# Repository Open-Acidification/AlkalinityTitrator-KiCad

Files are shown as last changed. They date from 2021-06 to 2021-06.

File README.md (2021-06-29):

# AlkalinityTitrator-KiCad
<!-- ALL-CONTRIBUTORS-BADGE:START - Do not remove or modify this section -->

<!-- ALL-CONTRIBUTORS-BADGE:END -->

KiCad files for pcb design for Open Acidification Alkalinity Titrator unit.

## Software Requirements

1. [KiCad](https://kicad.org/) - The PCB layout was created with KiCad which works on multiple platforms.

## Viewing and Editing the Schematic

1. Clone this repo to your local computer.
1. Open KiCad.
1. Use the KiCad menu to open the `full_project.pro` project file.
    * _File -> Open Project_
    * Navigate to your local repo location and select `full_project.pro` project file.
    * Double click the `full_project.sch` file on the left pane to open Eeschema.
1. View the Schematic.

## Viewing and Editing the PCB

1. Clone this repo to your local computer.
1. Open KiCad.
1. Use the KiCad menu to open the `full_project.pro` project file.
    * _File -> Open Project_
    * Navigate to your local repo location and select `full_project.pro` project file.
    * Double click the `full_project.kicad_pcb` file on the left pane to open Pcbnew.
1. View the PCB.

## Release

Each release has the appropriate binary Gerber (`.gbr`) and Drill (`.drl`) to be sent to the PCB board printing company.

We may have extra printed. Please contact us.

## Related Projects

* Micro Controller - [Alkalinity Titrator](https://github.com/Open-Acidification/AlkalinityTitrator) forms the brain of the device.
* PCB - __This repo__ holds the specifications for the PCB which connects various sensors.

## Contributors ✨

Thanks goes to these wonderful people ([emoji key](https://allcontributors.org/docs/en/emoji-key)):

<!-- ALL-CONTRIBUTORS-LIST:START - Do not remove or modify this section -->
<!-- prettier-ignore-start -->
<!-- markdownlint-disable -->
<table>
  <tr>
    <td align="center"><a href="https://github.com/KonradMcClure"><br /><sub><b>Konrad McClure</b></sub></a><br /><a href="https://github.com/Open-Acidification/AlkalinityTitrator-KiCad/commits?author=KonradMcClure" title="Code">💻</a></td>
    <td align="center"><a href="https://github.com/Noah-Griffith"><br /><sub><b>Noah-Griffith</b></sub></a><br /><a href="https://github.com/Open-Acidification/AlkalinityTitrator-KiCad/commits?author=Noah-Griffith" title="Code">💻</a></td>
  </tr>
</table>

<!-- markdownlint-restore -->
<!-- prettier-ignore-end -->

<!-- ALL-CONTRIBUTORS-LIST:END -->

This project follows the [all-contributors](https://github.com/all-contributors/all-contributors) specification. Contributions of any kind welcome!

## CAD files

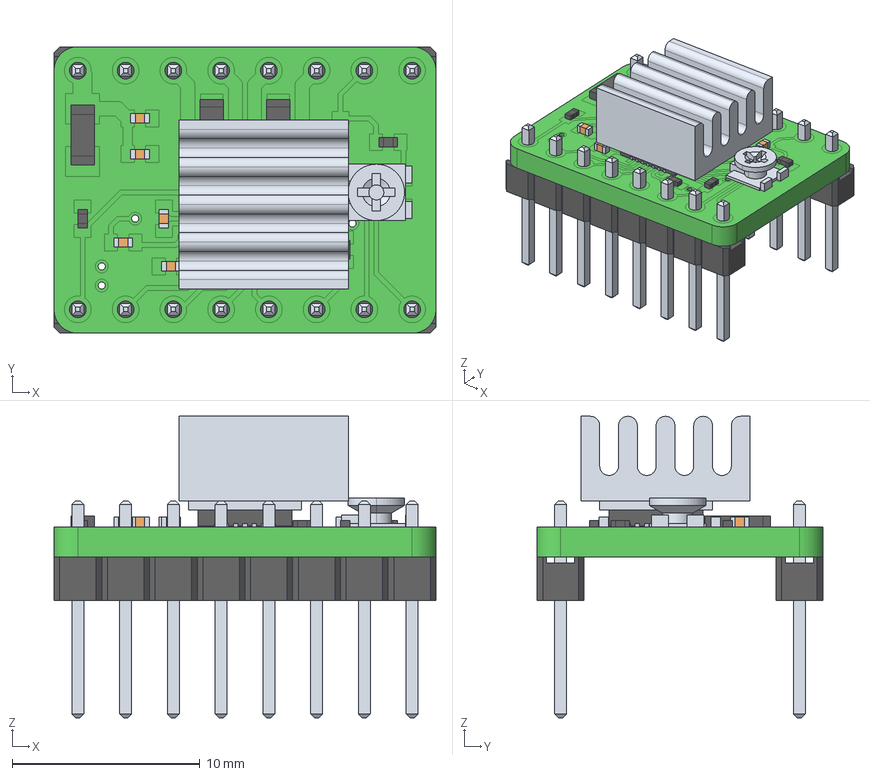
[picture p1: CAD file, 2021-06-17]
imported_3d/stepstick_asm.stp
20.3 x 15.2 x 16.0 mm
SCULPT1_1_-10289 x 6
SCULPT1_3_-13682 x 6
SCULPT1_2_-26742 x 6
0805_RESISTOR x 2
0402RES_RESISTOR0402RES x 4
LPATTERN1_1_ x 2
LPATTERN1_6_ x 2
LPATTERN1_7_ x 2
LPATTERN1_3_ x 2
LPATTERN1_2_ x 2
LPATTERN1_5_ x 2
LPATTERN1_8_ x 2
LPATTERN1_14_ x 2
LPATTERN1_10_ x 2
LPATTERN1_13_ x 2
LPATTERN1_4_ x 2
LPATTERN1_11_ x 2
LPATTERN1_9_ x 2
LPATTERN1_12_ x 2
SCULPT1_4_
SCULPT1_15_
SCULPT1_3_-1394
SCULPT1_1_-1765
SCULPT1_29_
SCULPT1_11_
SCULPT1_21_
SCULPT1_12_
SCULPT1_13_
SCULPT1_23_
SCULPT1_25_
SCULPT1_16_
SCULPT1_14_
SCULPT1_22_
SCULPT1_26_
SCULPT1_10_
SCULPT1_18_
SCULPT1_28_
SCULPT1_7_
SCULPT1_17_
SCULPT1_24_
SCULPT1_20_
SCULPT1_8_
SCULPT1_6_
SCULPT1_19_
SCULPT1_9_
SCULPT1_27_
SCULPT1_5_
SCULPT1_1_-7052
SCULPT1_2_-11434
SCULPT1_3_-28930
STEPSTICK-2620
HEATSINK_FOR_A4988
1206_CAP1206

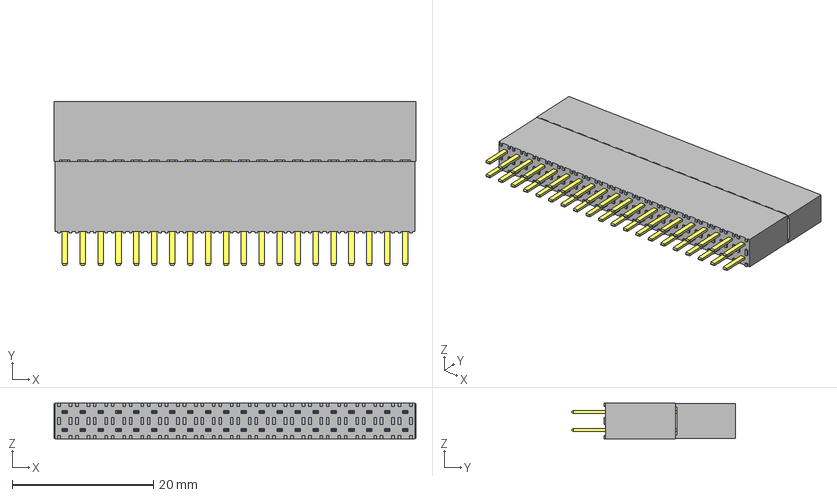
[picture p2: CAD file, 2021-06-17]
imported_3d/ESW-120-44-L-D.stp
51.3 x 23.2 x 5.08 mm
_ESW-120-44-L-D_socket
_ESW-120-44-L-D_pins
_ESW-120-44-L-D_bsocket

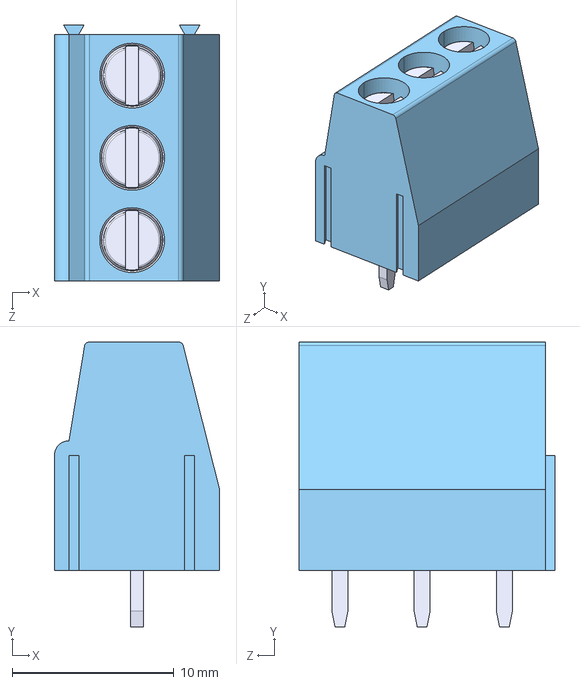
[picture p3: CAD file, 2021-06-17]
imported_3d/CUI_DEVICES_TB004-508-03BE.step
10.2 x 17.6 x 15.8 mm

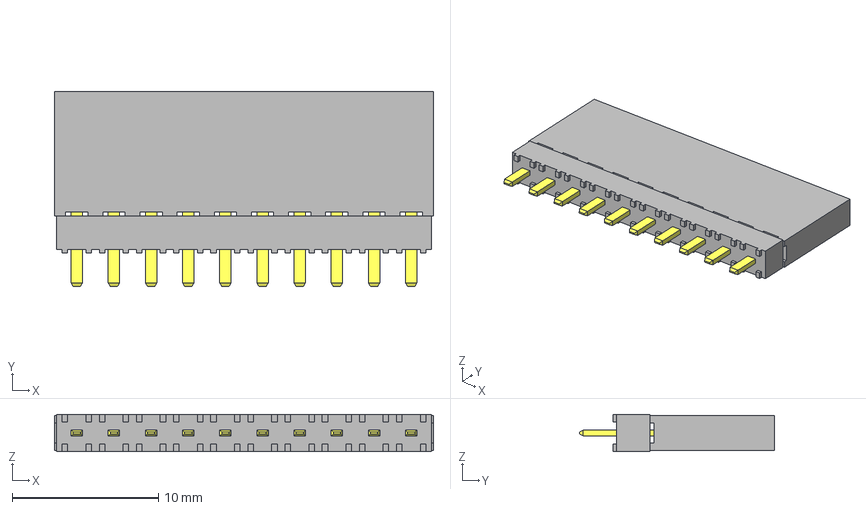
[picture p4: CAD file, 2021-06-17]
imported_3d/ESW-110-12-L-S.stp
25.9 x 13.3 x 2.54 mm
_ESW-110-12-L-S_socket
_ESW-110-12-L-S_pins
_ESW-110-12-L-S_bsocket

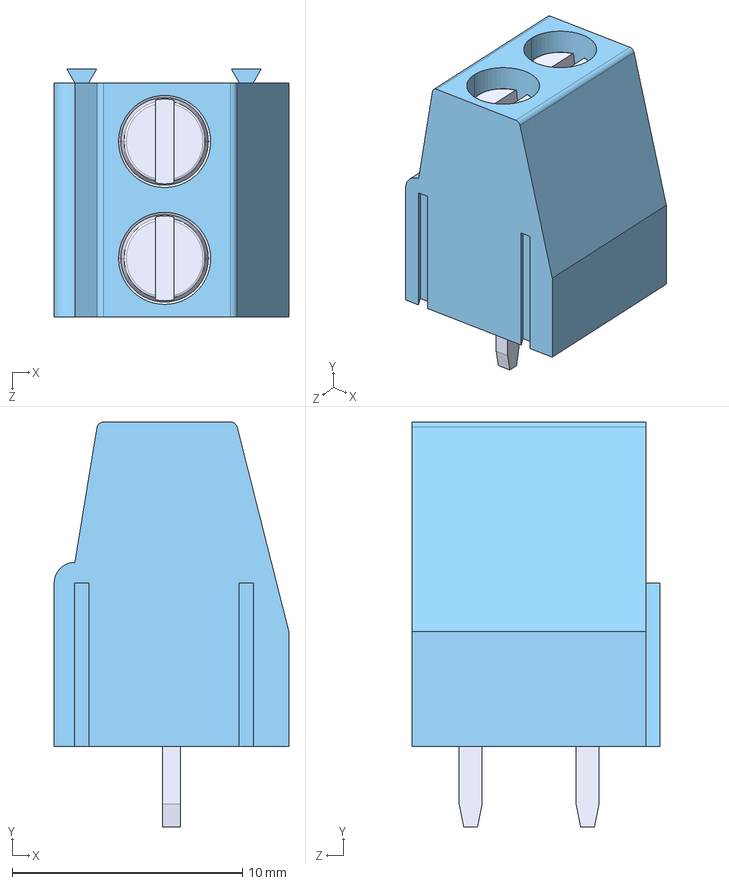
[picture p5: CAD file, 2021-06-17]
imported_3d/CUI_DEVICES_TB004-508-02BE.step
10.2 x 17.6 x 10.8 mm

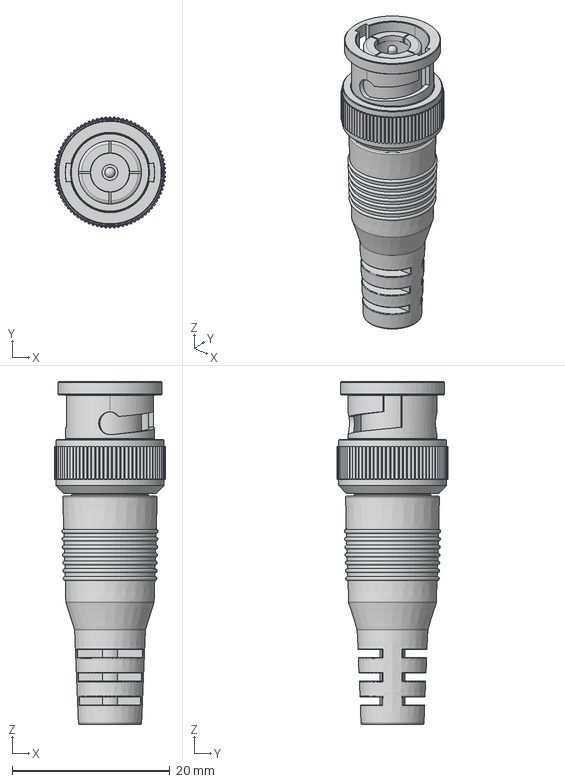
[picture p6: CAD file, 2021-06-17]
imported_3d/BNC-Connector-Straight.step
14.1 x 14.1 x 43.5 mm

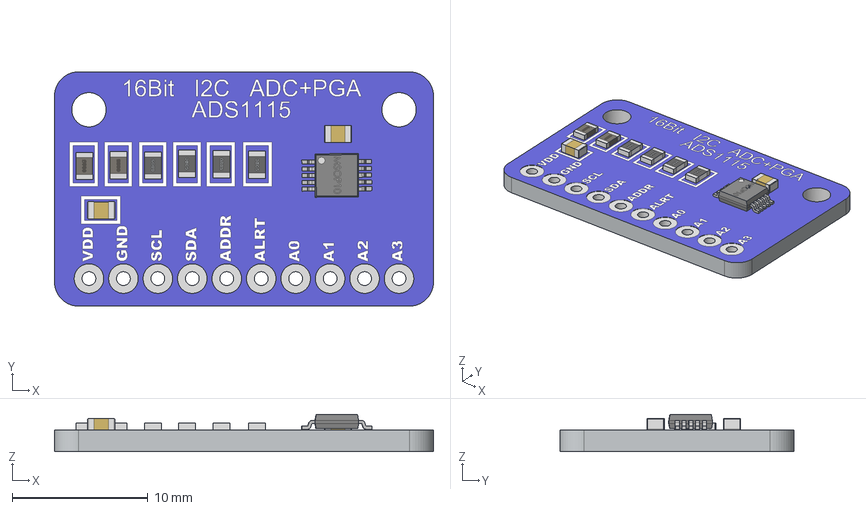
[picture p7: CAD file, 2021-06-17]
imported_3d/16Bit I2C ADC+PGA - ADS1115.stp
27.9 x 17.3 x 2.74 mm
ADS1115
0805 Capacitor x 2
0805 Inductor x 2
0805 Resistor x 4
MSOP10

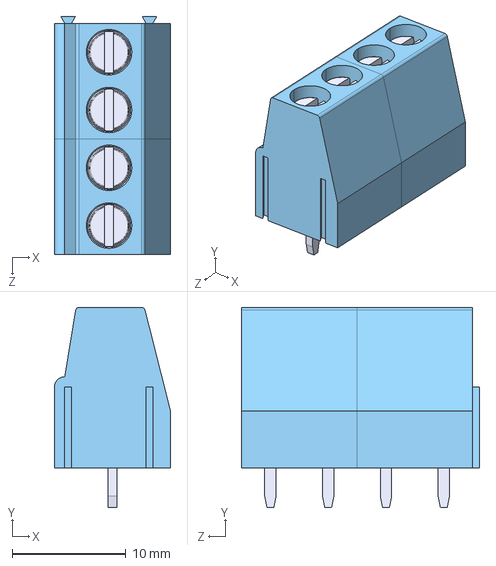
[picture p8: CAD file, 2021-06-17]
imported_3d/CUI_DEVICES_TB004-508-04BE.step
10.2 x 17.6 x 20.9 mm
TB004-508-02P_Blue - S x 2

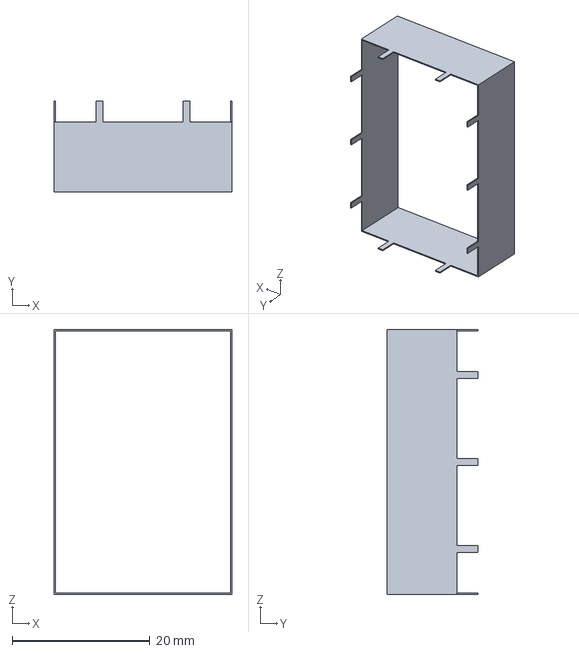
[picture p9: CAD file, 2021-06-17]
imported_3d/rf_shield2.stp
25.8 x 13.2 x 38.5 mm

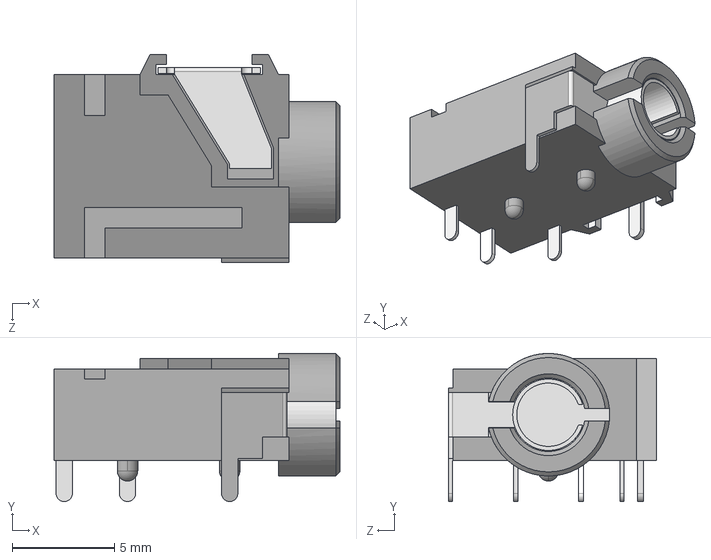
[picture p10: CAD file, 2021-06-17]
imported_3d/CUI_DEVICES_SJ-43515TS.step
14.0 x 7.25 x 10.2 mm

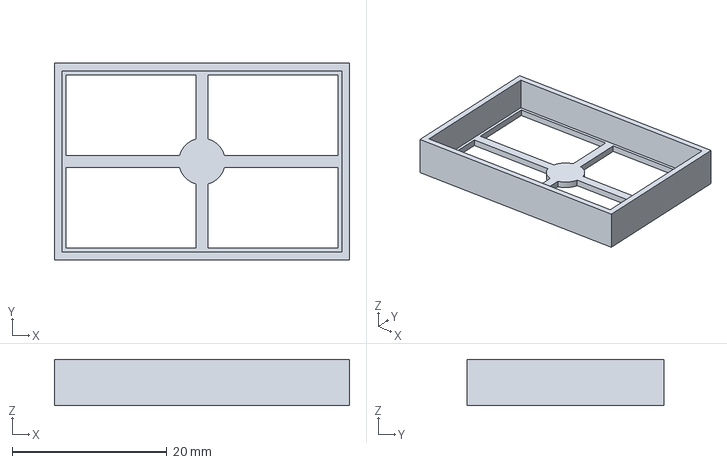
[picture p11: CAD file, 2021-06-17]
imported_3d/sms_205_f.stp
38.1 x 25.4 x 6.00 mm

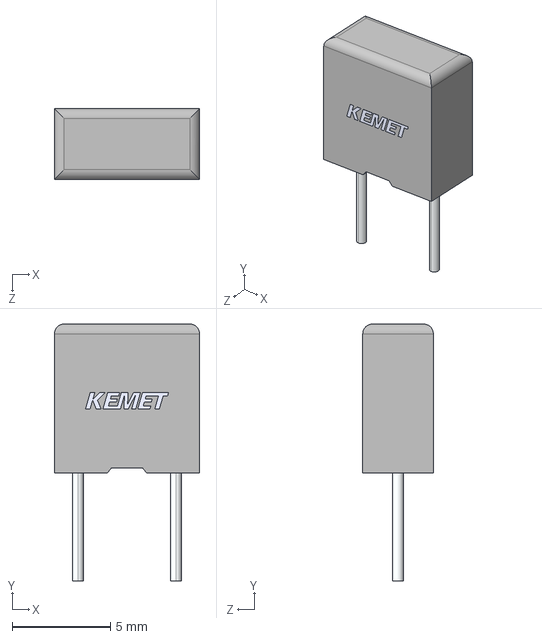
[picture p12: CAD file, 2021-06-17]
imported_3d/R82DC3330AA60K.step
7.40 x 13.1 x 3.60 mm

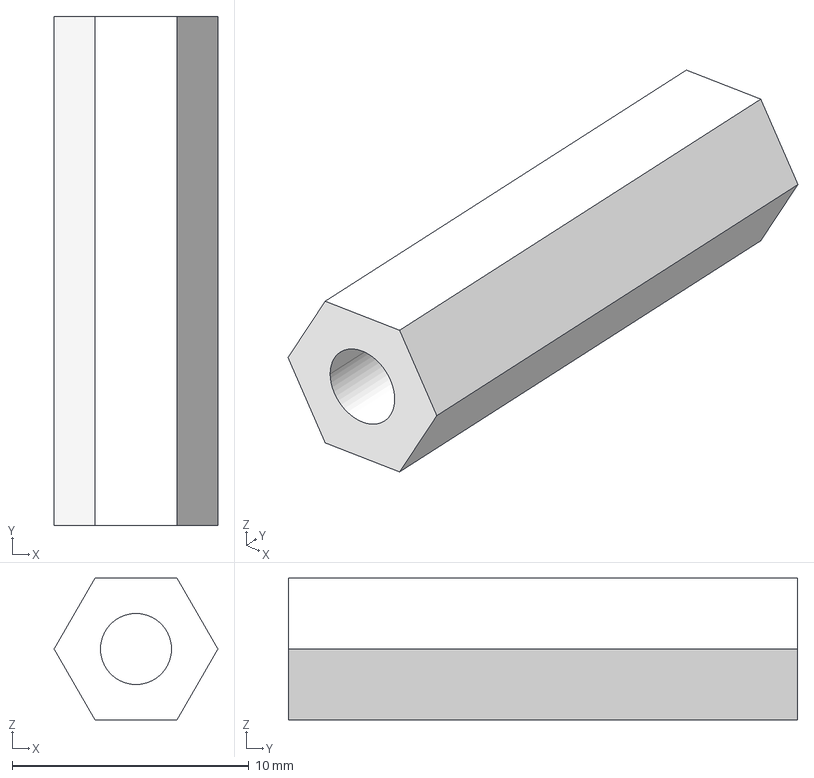
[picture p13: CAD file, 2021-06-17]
imported_3d/rasp_spacers.stp
6.92 x 21.5 x 5.99 mm

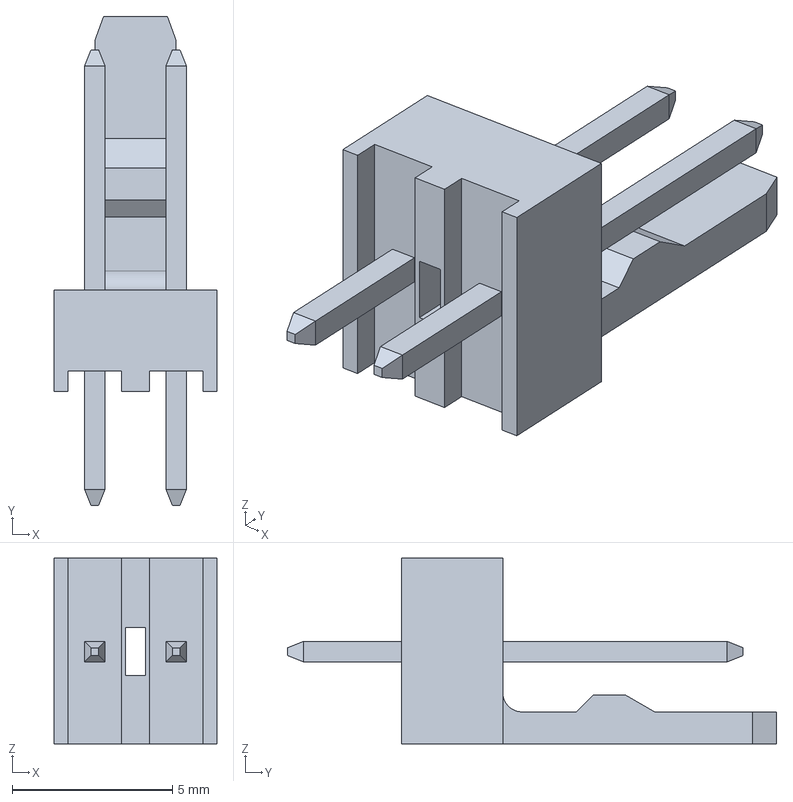
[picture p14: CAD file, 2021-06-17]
imported_3d/022272021.stp
5.08 x 15.3 x 5.80 mm

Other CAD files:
imported_3d/022053021.stp
imported_3d/705430112.stp
imported_3d/022053081.stp
imported_3d/022053161.stp
imported_3d/022272081.stp
imported_3d/705510007.stp
imported_3d/705550001.stp
imported_3d/705550050.stp
imported_3d/A4988BREAKOUT1.skp
imported_3d/M3x1.8mm Hex Nut.step
imported_3d/bd65496muv-single-brushed-dc-motor-driver-carrier.step
imported_3d/max31865_nopins.stp

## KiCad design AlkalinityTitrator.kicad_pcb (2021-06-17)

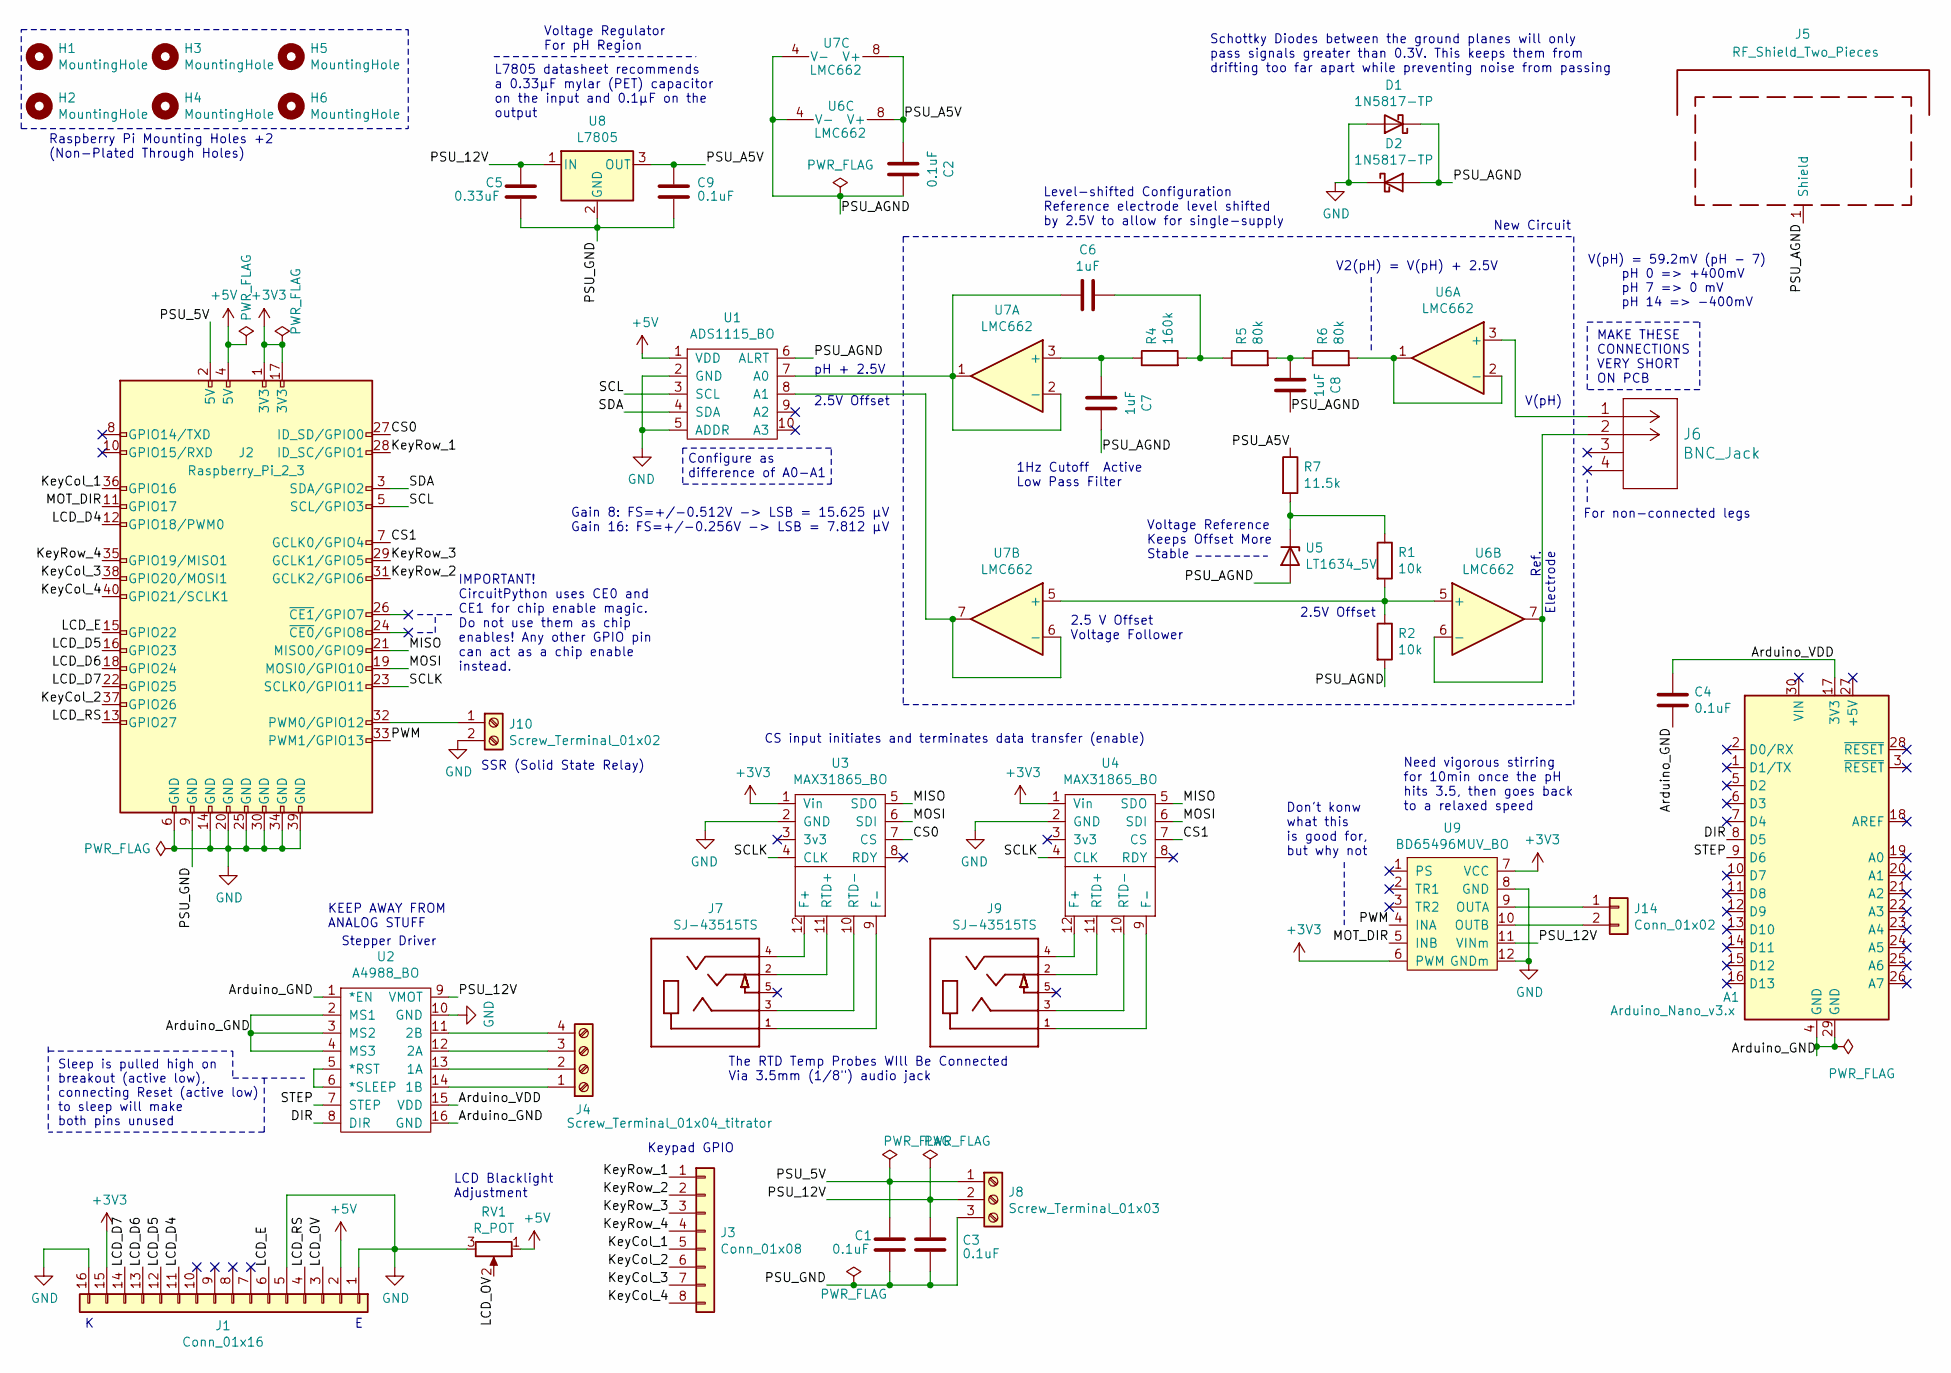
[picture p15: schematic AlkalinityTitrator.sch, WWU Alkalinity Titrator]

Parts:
A1: Arduino_Nano_v3.x; Arduino_Nano
C1, C2, C3, C4: 0.1uF; C_Disc_D3.8mm_W2.6mm_P2.50mm
C5: 0.33uF; C_Rect_L7.2mm_W3.5mm_P5.00mm_FKS2_FKP2_MKS2_MKP2
C6, C7, C8: 1uF; C_Disc_D3.8mm_W2.6mm_P2.50mm
C9: 0.1uF; C_Rect_L7.2mm_W3.5mm_P5.00mm_FKS2_FKP2_MKS2_MKP2
D1, D2: 1N5817-TP; D_DO-41_SOD81_P7.62mm_Horizontal
H1, H2, H3, H4, H5, H6: MountingHole; MountingHole_3mm
J1: Conn_01x16; PinHeader_1x16_P2.54mm_Horizontal
J2: Raspberry_Pi_2_3; RaspberryPi
J3: Conn_01x08; PinHeader_1x08_P2.54mm_Horizontal
J4: Screw_Terminal_01x04_titrator; TerminalBlock_bornier-4_P5.08mm
J5: RF_Shield_Two_Pieces; SMS-205_LeaderTech_RFShield
J6: BNC_Jack
J7, J9: SJ-43515TS; CUI_SJ-43515TS; PART_REV 1.04
J8: Screw_Terminal_01x03; TerminalBlock_bornier-3_P5.08mm
J10: Screw_Terminal_01x02; TerminalBlock_bornier-2_P5.08mm
J14: Conn_01x02; PinHeader_1x02_P2.54mm_Horizontal
R1, R2: 10k; R_Axial_DIN0207_L6.3mm_D2.5mm_P7.62mm_Horizontal
R4: 160k; R_Axial_DIN0207_L6.3mm_D2.5mm_P7.62mm_Horizontal
R5, R6: 80k; R_Axial_DIN0207_L6.3mm_D2.5mm_P7.62mm_Horizontal
R7: 11.5k; R_Axial_DIN0207_L6.3mm_D2.5mm_P7.62mm_Horizontal
RV1: R_POT; Potentiometer_Piher_PT-6-V_Vertical
U1: ADS1115_BO; ADS1115_BO_Footprint
U2: A4988_BO; A4988_BO_Footprint
U3, U4: MAX31865_BO; MAX31865
U5: LT1634_5V; TO-92_Inline
U6, U7: LMC662; DIP-8_W7.62mm
U8: L7805; 78XXS
U9: BD65496MUV_BO; BD65496MUV_BO_Footprint

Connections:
+3V3: J1.15, J2.1 (3V3), J2.17 (3V3), U3.1 (Vin), U4.1 (Vin), U9.6 (PWM), U9.7 (VCC)
+5V: J1.2, J2.4 (5V), RV1.1, U1.1 (VDD)
/Arduino_GND: A1.4 (GND), A1.29 (GND), C4.2, U2.1 (*EN), U2.2 (MS1), U2.3 (MS2), U2.4 (MS3), U2.16 (GND)
/Arduino_VDD: A1.17 (3V3), C4.1, U2.15 (VDD)
/CS0: J2.27 (ID_SD/GPIO0), U3.7 (CS)
/CS1: J2.7 (GCLK0/GPIO4), U4.7 (CS)
/DIR: A1.8 (D5), U2.8 (DIR)
/KeyCol_1: J2.36 (GPIO16), J3.5
/KeyCol_2: J2.37 (GPIO26), J3.6
/KeyCol_3: J2.38 (GPIO20/MOSI1), J3.7
/KeyCol_4: J2.40 (GPIO21/SCLK1), J3.8
/KeyRow_1: J2.28 (ID_SC/GPIO1), J3.1
/KeyRow_2: J2.31 (GCLK2/GPIO6), J3.2
/KeyRow_3: J2.29 (GCLK1/GPIO5), J3.3
/KeyRow_4: J2.35 (GPIO19/MISO1), J3.4
/LCD_D4: J1.11, J2.12 (GPIO18/PWM0)
/LCD_D5: J1.12, J2.16 (GPIO23)
/LCD_D6: J1.13, J2.18 (GPIO24)
/LCD_D7: J1.14, J2.22 (GPIO25)
/LCD_E: J1.6, J2.15 (GPIO22)
/LCD_OV: J1.3, RV1.2
/LCD_RS: J1.4, J2.13 (GPIO27)
/MISO: J2.21 (MISO0/GPIO9), U3.5 (SDO), U4.5 (SDO)
/MOSI: J2.19 (MOSI0/GPIO10), U3.6 (SDI), U4.6 (SDI)
/MOT_DIR: J2.11 (GPIO17), U9.5 (INB)
/PSU_5V: C1.1, J2.2 (5V), J8.1
/PSU_12V: C3.1, C5.1, J8.2, U2.9 (VMOT), U8.1 (IN), U9.11 (VINm)
/PSU_A5V: C2.1, C9.1, R7.1, U6.8 (V+), U7.8 (V+), U8.3 (OUT)
/PSU_AGND: C2.2, C7.2, C8.2, D1.1 (K), D2.2 (A), J5.1, R2.2, U1.6 (ALRT), U5.1 (A), U6.4 (V-), U7.4 (V-)
/PSU_GND: C1.2, C3.2, C5.2, C9.2, J2.9 (GND), J8.3, U8.2 (GND)
/PWM: J2.33 (PWM1/GPIO13), U9.4 (INA)
/SCL: J2.5 (SCL/GPIO3), U1.3 (SCL)
/SCLK: J2.23 (SCLK0/GPIO11), U3.4 (CLK), U4.4 (CLK)
/SDA: J2.3 (SDA/GPIO2), U1.4 (SDA)
/STEP: A1.9 (D6), U2.7 (STEP)
GND: D1.2 (A), D2.1 (K), J1.1, J1.5, J1.16, J2.6 (GND), J2.14 (GND), J2.20 (GND), J2.25 (GND), J2.30 (GND), J2.34 (GND), J2.39 (GND), J10.2, RV1.3, U1.2 (GND), U1.5 (ADDR), U2.10 (GND), U3.2 (GND), U4.2 (GND), U9.8 (GND), U9.12 (GNDm)
unnamed: C6.1, U1.7 (A0), U7.1, U7.2 (-)
unnamed: C6.2, R4.2, R5.1
unnamed: C7.1, R4.1, U7.3 (+)
unnamed: C8.1, R5.2, R6.1
unnamed: J4.1 (2B), U2.14 (1B)
unnamed: J4.2 (2A), U2.13 (1A)
unnamed: J4.3 (1A), U2.12 (2A)
unnamed: J4.4 (1B), U2.11 (2B)
unnamed: J6.1, U6.3 (+)
unnamed: J6.2, U6.6 (-), U6.7
unnamed: J7.1, U3.9 (F-)
unnamed: J7.2, U3.11 (RTD+)
unnamed: J7.3, U3.10 (RTD-)
unnamed: J7.4, U3.12 (F+)
unnamed: J9.1, U4.9 (F-)
unnamed: J9.2, U4.11 (RTD+)
unnamed: J9.3, U4.10 (RTD-)
unnamed: J9.4, U4.12 (F+)
unnamed: J2.32 (PWM0/GPIO12), J10.1
unnamed: J14.1, U9.9 (OUTA)
unnamed: J14.2, U9.10 (OUTB)
unnamed: R1.1, R7.2, U5.2 (K)
unnamed: R1.2, R2.1, U6.5 (+), U7.5 (+)
unnamed: R6.2, U6.1, U6.2 (-)
unnamed: U1.8 (A1), U7.6 (-), U7.7
unnamed: U2.5 (*RST), U2.6 (*SLEEP)

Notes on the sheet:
Stepper Driver
Sleep is pulled high on breakout (active low), connecting Reset (active low) to sleep will make both pins unused
Need vigorous stirring for 10min once the pH hits 3.5, then goes back to a relaxed speed
KEEP AWAY FROM ANALOG STUFF
Gain 8: FS=+/-0.512V -> LSB = 15.625 μV Gain 16: FS=+/-0.256V -> LSB = 7.812 μV
Level-shifted Configuration Reference electrode level shifted by 2.5V to allow for single-supply
MAKE THESE CONNECTIONS VERY SHORT ON PCB
V(pH) = 59.2mV (pH - 7) pH 0 => +400mV pH 7 => 0 mV pH 14 => -400mV
V2(pH) = V(pH) + 2.5V
Ref. Electrode
V(pH)
New Circuit
Keypad GPIO
LCD Blacklight Adjustment
CS input initiates and terminates data transfer (enable)
Raspberry Pi Mounting Holes +2 (Non-Plated Through Holes)
The RTD Temp Probes WIll Be Connected Via 3.5mm (1/8") audio jack
SSR (Solid State Relay)
IMPORTANT! CircuitPython uses CE0 and CE1 for chip enable magic. Do not use them as chip enables! Any other GPIO pin can act as a chip enable instead.
pH + 2.5V
2.5V Offset
2.5 V Offset Voltage Follower
Configure as difference of A0-A1
1Hz Cutoff Active Low Pass Filter
Voltage Regulator For pH Region
Voltage Reference Keeps Offset More Stable
Don't konw what this is good for, but why not
For non-connected legs
Schottky Diodes between the ground planes will only pass signals greater than 0.3V. This keeps them from drifting too far apart while preventing noise from passing
L7805 datasheet recommends a 0.33μF mylar (PET) capacitor on the input and 0.1μF on the output

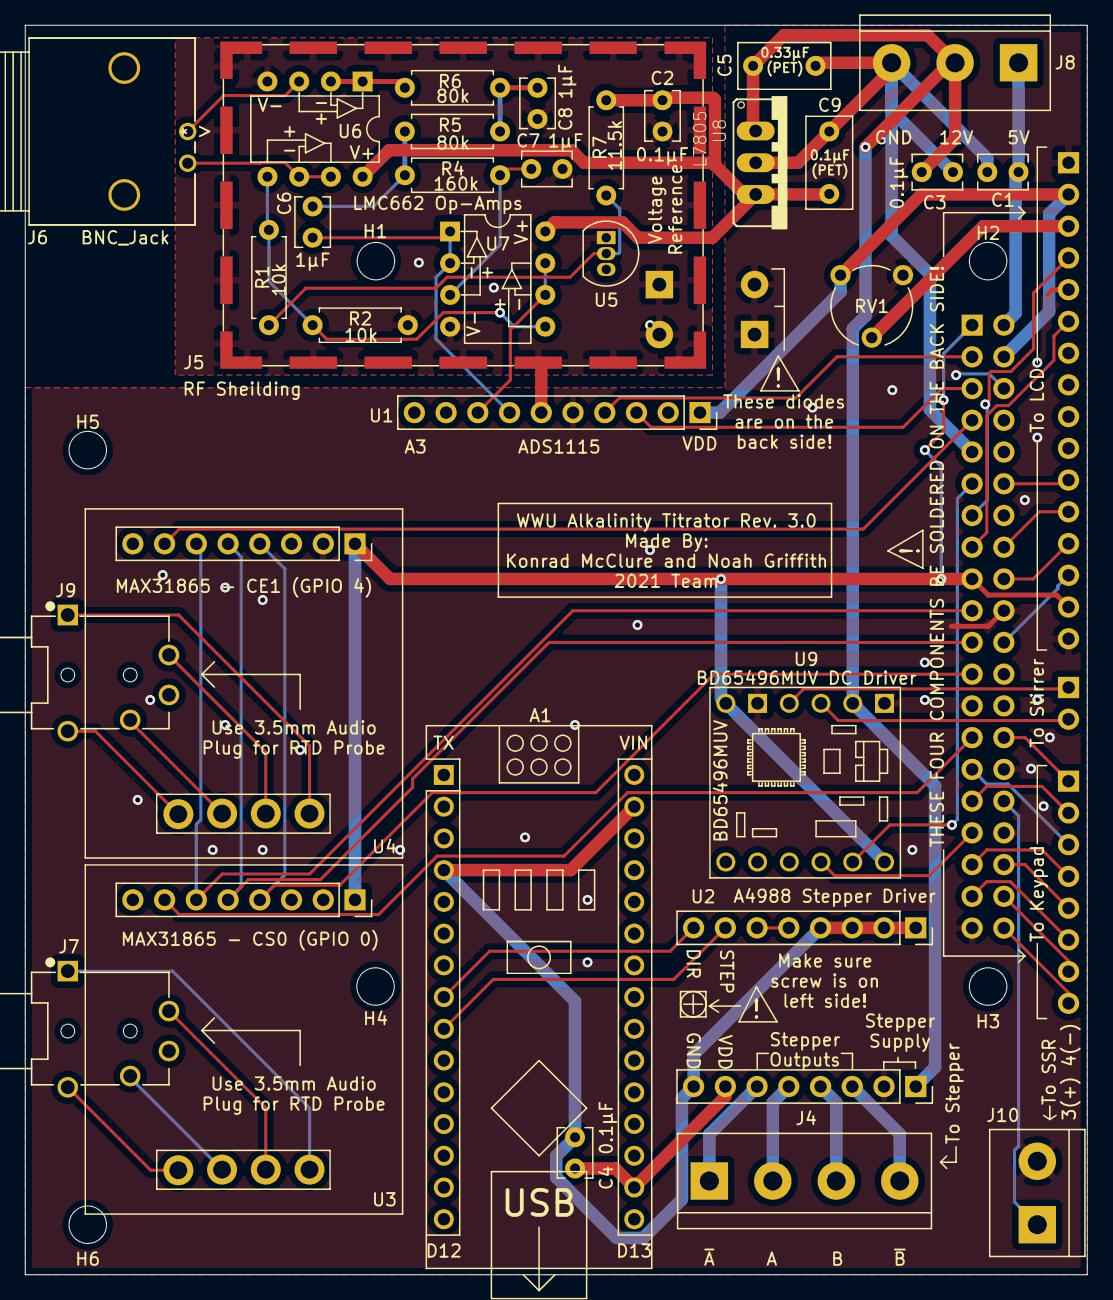
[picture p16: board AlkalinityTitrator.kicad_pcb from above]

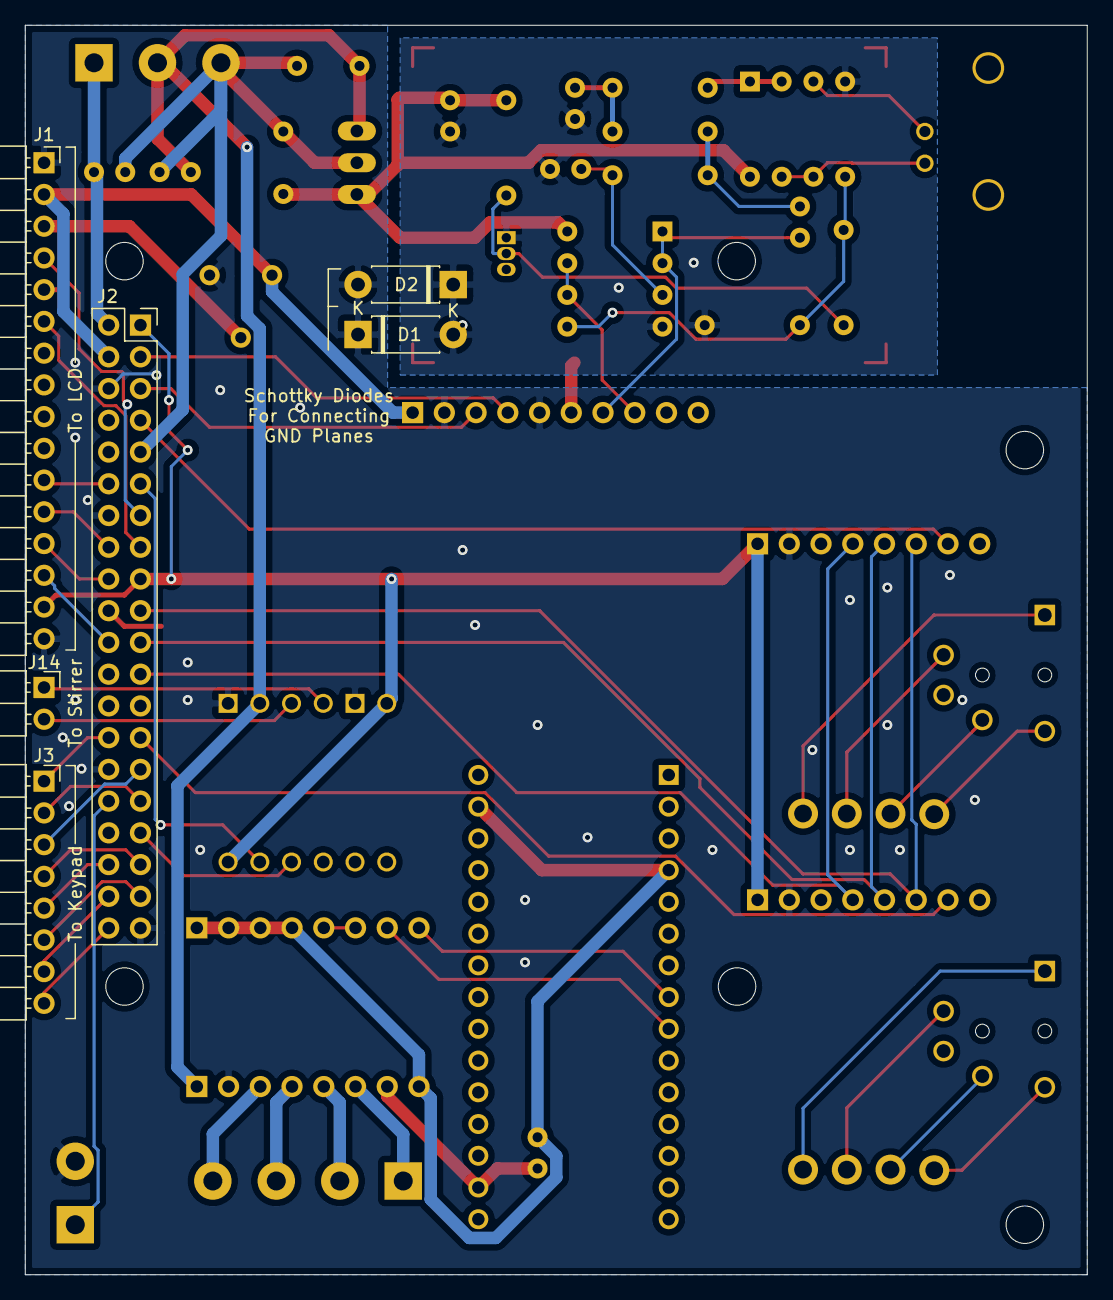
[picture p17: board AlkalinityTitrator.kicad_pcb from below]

Board: 2 copper layers, 85.0 x 100.0 mm, 45 parts (6 on the bottom side), 62 nets.

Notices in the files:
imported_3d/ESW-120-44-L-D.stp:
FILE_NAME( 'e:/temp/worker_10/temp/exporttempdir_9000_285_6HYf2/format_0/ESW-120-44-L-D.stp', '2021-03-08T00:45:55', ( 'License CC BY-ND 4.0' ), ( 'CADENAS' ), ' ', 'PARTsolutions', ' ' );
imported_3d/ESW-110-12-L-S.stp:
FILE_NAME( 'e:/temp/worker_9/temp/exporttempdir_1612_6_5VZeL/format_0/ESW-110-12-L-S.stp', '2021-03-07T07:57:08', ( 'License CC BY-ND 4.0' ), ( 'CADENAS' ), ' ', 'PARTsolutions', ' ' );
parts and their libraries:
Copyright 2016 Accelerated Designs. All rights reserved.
